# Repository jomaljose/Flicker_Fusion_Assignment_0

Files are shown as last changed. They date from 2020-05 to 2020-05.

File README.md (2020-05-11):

# Flicker Fusion Threshold 
### Embedded system assignment 0

## AIM

Set up a prototype of an Embedded System for the measurement of a person’s subjective flicker fusion threshold using Teensy 3.2 board. An LED with varying blinking frequency is used as stimulus and when it reaches the threshold flicker fusion frequency, the current frequency should be displayed in a serial monitor on a connected PC.

## INTRODUCTION

*"The **flicker fusion threshold**, is a concept in the psycho-physics of vision. It is defined as the frequency at which an intermittent light stimulus appears to be completely steady to the average human observer. Flicker fusion threshold is related to persistence of vision."*
##### Flicker Fusion Threshold https://en.wikipedia.org/wiki/Flicker_fusion_threshold
In this project I used a Teensy 3.2, a push button, 390 ohm resistor and LED to create a prototype. The frequency of LED blinking is continuously increasing in my prototype.  The flicker fusion frequency is displayed using serial monitor of VSCode when the push button is pressed.

## METHODS
### Hardware Description

#### Components

 1. Teensy 3.2
 2. 390 ohm resistor
 3. Push button
 4. Wires
 5. Breadboard

#### Pull up resistor calculation

The equation to find the resistance of a pullup resistor
R = (Vs-Vf)/If
According to the [Teensy 3.2 data card](https://github.com/jomaljose/Flicker_Fusion_Assignment_0/blob/master/Datasheet/Teensy%203_2%20card%20%20.pdf)the input voltage of Teensy board is 3.3 - 6 Volts.The output voltage of Teensy 3.2 board is 3.3V. The typical Vf of a red LED is 1.8 to 2.1Volts. The safe operating forward current through this led is taken as 10mA. <br/>
 Then, <br/>
(3.3-1.8)/10mA = 150ohm <br/>
Therefore for the safe operation of LED the pullup resistance should be greater than 150 ohm. The pullup resistor used in this circuit is 390 ohm.

#### Push Button

The mechanical push button may produce errors in switching therefore we have written codes for debouncing and enabled input pullup resistor internally in teensy 3.2.

### Circuit
The push button is connected to the D5 pin of Teensy 3.2 and GND pin. Led is connected to the D12 pin and GND.
It is also explained in this Youtube video:
https://youtu.be/GUNod7JRGfk

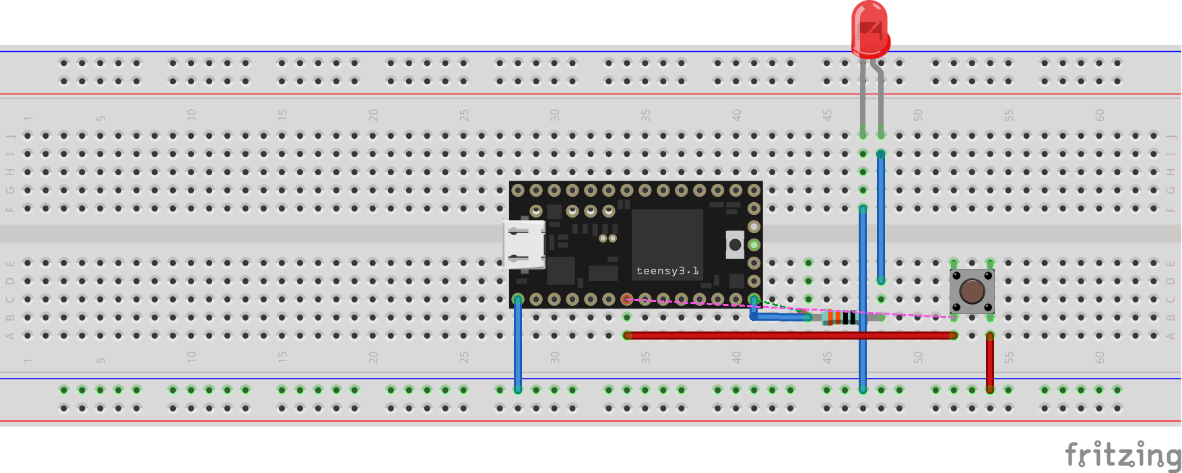
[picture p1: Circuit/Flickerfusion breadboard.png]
Breadboard representation of circuit

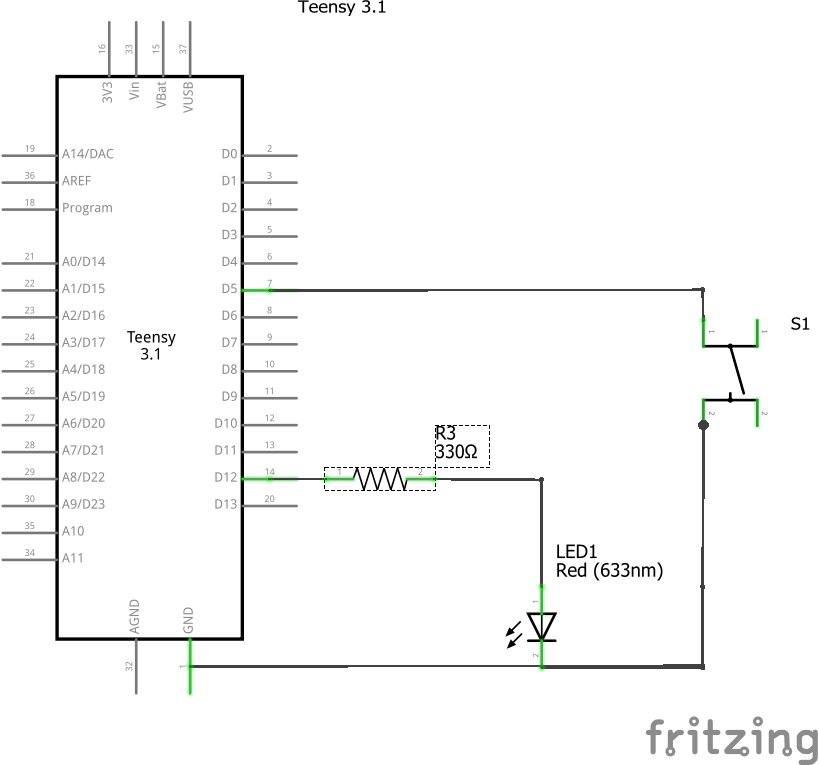
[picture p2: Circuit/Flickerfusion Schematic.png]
Schematic Diagram

### [Software](https://github.com/jomaljose/Flicker_Fusion_Assignment_0/blob/master/Flicker_fusion/src/main.cpp)
 VSCode with Platform IO extension is used to code in this project. The pin 12 and 5 is defined as *ledpin* and *buttonpin* respectively. Internal pullup resistor is enabled by `pinMode(buttonpin, INPUT_PULLUP)` for the button pin. The frequency of led is varied from 0.5Hz to 90Hz using if loop. When the Flicker fusion frequency reaches, the person will press the button and it will trigger the interrupt. In the interrupt routine function, frequency at that time is displayed on the serial monitor along with time period in millisecond. Interrupt is triggered on the falling edge of the switching action. 
 
### Output Waveform Display
The waves generated is, by serial printing the led state and plotting it using [Serialplot](https://hackaday.io/project/5334-serialplot-realtime-plotting-software) software. 
## [RESULT](https://github.com/jomaljose/Flicker_Fusion_Assignment_0/tree/master/Output)
The flicker fusion threshold frequency is printed on the serial monitor when the button is pressed.
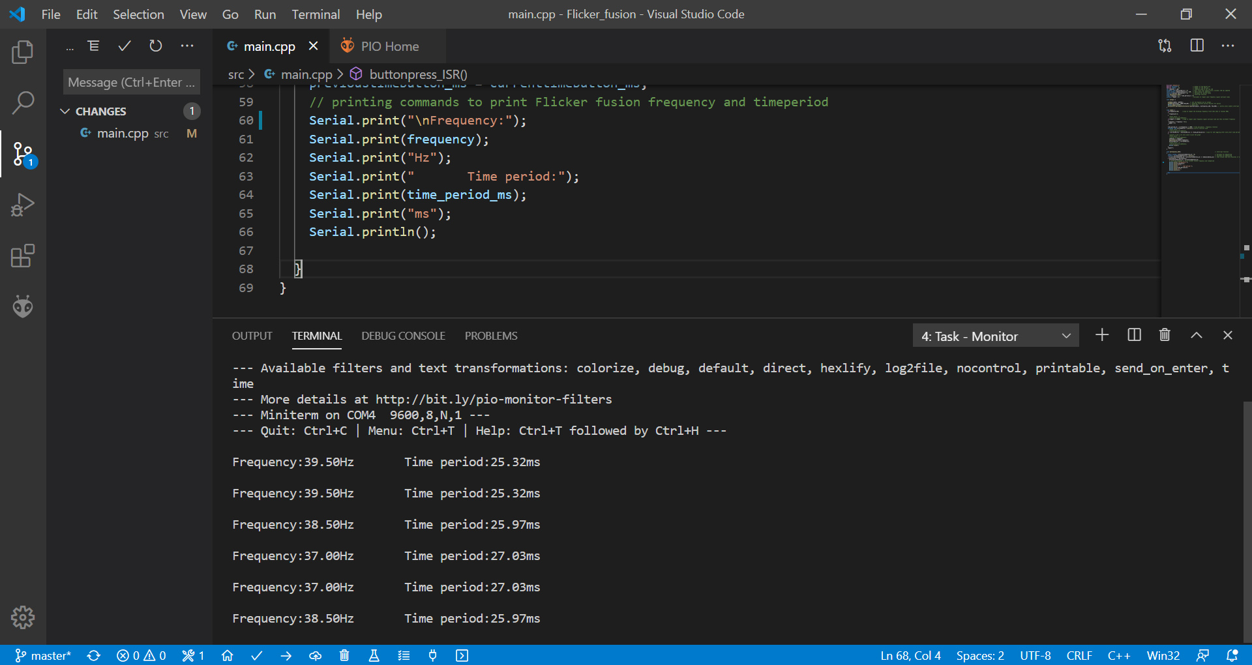
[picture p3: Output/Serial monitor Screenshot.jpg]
Screenshot of VSCode serial monitor


The output is verified by plotting the led state by using Serial plot software.
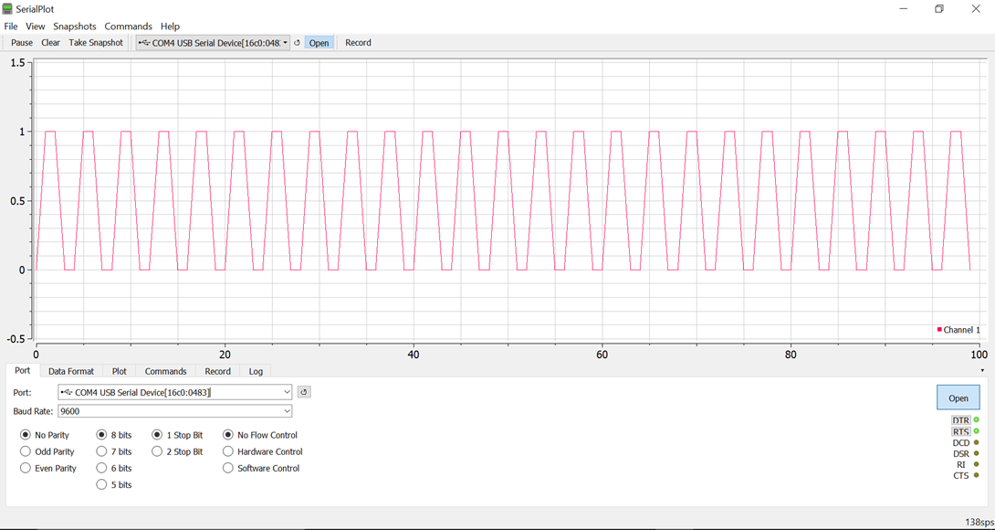
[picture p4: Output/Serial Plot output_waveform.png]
Screenshot of Serialplot software at iption hereherehere

This waveform is plotted at 35Hz frequency. The plotted waveform consist of 4 samples in every wave cycle. In the above figure at right corner of the serial plot window SPS (samples per second) is shown. By dividing the SPS by 4 we get the frequency of the plotted waveform.
In this case the SPS is 138
Therefore the frequency of the plotted waveform will be 138/4 = **34.5Hz**.
## FUTURE SCOPE & LIMITATIONS
The current prototype is giving flicker fusion threshold frequency value almost similar to the theoretical value of human flicker fusion threshold frequency. Eventhough,the plotted waveform have some error with the actual serial printed frequency. In future I like to eliminate this error and make it available for primary school teachers, because it will be helpful for them to teach persistence of vision.

## CONCLUSION

Human  flicker fusion threshold was tested successfully using this prototype. My conclusion after several tests is that my flicker fusion threshold frequency is between 37-39.5Hz.

This project gave me the opportunity to get into GitHub, Teensy 3.2 and different IDEs etc.

## REFERENCES

 1. Wikipedia contributors. (2020, January 29). Flicker fusion threshold. Retrieved from https://en.wikipedia.org/wiki/Flicker_fusion_threshold
 2. Teensyduino: Using the UART (real serial) with Teensy on the Arduino IDE. (2020). Retrieved from https://www.pjrc.com/teensy/td_uart.html
 3. Vishay Semiconductors. (2019). _TLUR6400, TLUR6401 datasheet_ (2019 revised ed.), Vishay Semiconductors.

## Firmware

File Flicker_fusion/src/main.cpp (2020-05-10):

#include <Arduino.h>
#define buttonpin 5                     // Number of the Button pin
#define ledPin    12                    // Number of the LED pin
int ledState = LOW;                     // LedState used to set the LED
unsigned long previousMillis = 0;       // Will store last time(in milli seconds) LED was updated
const uint32_t debouncedelay_ms = 150;  // Small delay for debounce
volatile boolean buttonpress = 0;       // Variable for button state
void buttonpress_ISR();                 // Interrupt function
float frequency = 0.5, time_period_ms = 0; 
uint16_t repeat = 0;                    //variable to repeat same frequency signal multiple times

void setup() {
  
  pinMode(ledPin, OUTPUT);          // set the digital pin as output
  pinMode(buttonpin, INPUT_PULLUP); // Enabling internal pullup resistor for button
  Serial.begin(9600);             // Baud rate
  attachInterrupt(digitalPinToInterrupt(buttonpin), buttonpress_ISR, FALLING); // button press enable interrupt function 'buttonpress_ISR'
}

void loop() {
  if(frequency==90)     //Loop to repeat the blinking frequency from 0.5Hz when it reaches 90Hz
  {
    frequency=0.5;
  }
    //Plot point - 1
    //Serial.println(ledState); 
  if(repeat == 15000)   //Lopp to repeat same frequency signal multiple time and then increment frequency
  {
   frequency = frequency + 0.5;
   repeat = 0;
  }
 
  time_period_ms = (1/frequency) * 1000; //Time period(ms), frequensy relation
  unsigned long currentMillis = millis();//millis function used
    //Plot point - 2
    //Serial.println(ledState);
  if (currentMillis - previousMillis >= (time_period_ms/2)) //Loop for LED toggling after every half time period
  {
    //points 3 and 4 are only used to plot the graph
    //Plot point - 3
    //Serial.println(ledState);        
    ledState = !ledState;
    digitalWrite(ledPin,ledState);
    previousMillis = currentMillis;
    //Plot point - 4 
    //Serial.println(ledState);
    Serial.flush();
  }
  repeat++;
}

void buttonpress_ISR()                                                    // Interrupt function
{
  static uint32_t previoustimebutton_ms = 0;                              // Variable for debouncing
  uint32_t currenttimebutton_ms = millis();                               // Variable for debouncing
   if((currenttimebutton_ms - previoustimebutton_ms) >= debouncedelay_ms) // Code inside loop only executes if buttonpress time is greater than debounce delay_ms
  { buttonpress = !buttonpress;
    previoustimebutton_ms = currenttimebutton_ms;
    // printing commands to print Flicker fusion frequency and timeperiod
    Serial.print("\nFrequency:");
    Serial.print(frequency);
    Serial.print("Hz");
    Serial.print("       Time period:");
    Serial.print(time_period_ms);
    Serial.print("ms");
    Serial.println();
        
  }
}
